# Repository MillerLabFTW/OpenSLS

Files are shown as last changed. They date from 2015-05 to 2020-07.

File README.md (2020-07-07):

# OpenSLS

#### An open-source Selective Laser Sintering platform developed at Rice University
#### Miller Lab: Physiologic Systems Engineering and Advanced Materials
#### [millerlab.rice.edu](http://millerlab.rice.edu)
&nbsp;

### Update 07/07/20
- Our latest work has been published in Nature Biomedical Engineering. Here, we adapted openSLS for laser sintering of carbohydrates, which we are using to pattern perfusable vascular networks in engineered tissues
- Learn more about this work from Rice University's [Press Release](http://news.rice.edu/2020/06/29/laser-welded-sugar-sweet-way-to-3d-print-blood-vessels-2/?fbclid=IwAR0U7sia3JYhuekfoaQjJkxIh-vBjE8x_2c2UG4KTCaLtkVJyBe03XaeHhM) or by reading [the article](https://rdcu.be/b5tHy).
- The R4 hardware designs are the final versions developed in this work

### Update 03/23/20
- We are adding a new batch of design files for openSLS -- more details to come
- Please note that the newly added R4 design is *NOT* simply an upgrade of our earlier R3 hardware. Rather, it is a version for SLS using specialty powders for biomaterials research, and uses a different mechanism for powder handling. We will add more details about this (hopefully soon!). For conventional nylon or wax SLS, R3 remains the most recent design. 

### Update 02/10/16
- We are excited to annouce that OpenSLS has been published! You can find our paper at [PLOS ONE's website](http://journals.plos.org/plosone/article?id=10.1371/journal.pone.0147399).
Many of the hardware-related details (wiring diagrams, G-code editing, Bill of Materials) are in the supporting information, which we have uploaded here.  
- We are releasing our R3 hardware update and the corresponding firmware. What's new? See below.
- A Python version of our G-code munging utility is now available, which may be more convenient than our earlier PHP implementation

### Build Documentation
This git repository includes:
- Designs for lasercut and 3D printed parts for our first (R1), second (R2), and third (R3) generations of powder handing modules
- Current firmware (with thanks to Tim Schmidt!)
- Slic3r configuration and G-code munging script for G-code creation and processing
- Wiring diagram for electronics configuration (based on RAMBo electronics)
- Model geometries we showcased in our PLOS ONE paper
- Bill of Materials

### Hardware Versions
Basic summary of our hardware verions to date:

1. R1, designed by Andreas Bastian: Proof-of-concept build for OpenSLS. Buld is almost entirely acrylic + 3D printed parts. Powder distributor is a metal rod which counter-rotates, driven by belt motion. This build has everything you need to do SLS, but it lacks a simple powder collection system.
2. R2, designed by Andreas Bastian: This was the hardware used for the entirety of our PLOS ONE paper. It is mostly made from acrylic, but has an aluminum build piston and platform amenable to heating. Distributor is a static plow (a lab spatula). Powder is collected into a hopper through ducts built into the acrylic design.
You can read more about the design upgrades Andreas made from R1 hardware to R2 hardware on the [RepRap wiki page](http://reprap.org/wiki/OpenSLS#R1_Hardware). 
3. R3, designed by Ian Kinstlinger, Anderson Ta, and David Yalacki: This is an all-acrylic build designed for low cost and simplicity. Larger powder ducts facilitate powder collection and the overall form factor is a bit smaller. Note that this build will not be compatible with any powder pre-heating, but it's been working great for our purposes. Distributor is a steel 8mm rod mounted on a pair of 608 bearings. A [DC Motor](http://www.amazon.com/Science-Wiz-Motors-Working-Voltage/dp/B000BRUHW8/ref=sr_1_2?ie=UTF8&qid=1455162773&sr=8-2&keywords=dc+motor) spins the rod to give you a rotating distributor and the whole thing is mounted on springs to adjust height.
4. R4, designed by Ian Kinstlinger and David Yalacki: This is our modified build for carbohydrate sintering. We replace the conventional two-piston design (powder reservoir and build volume) with a single piston build volume and a powder reservoir which is suspended from the 2-axis gantry which moves the laser head around. Powder is dispensed by shaking it loose from the reservoir onto the build area. 
This design helps to mitigate the relatively poor powder flowability of carbohydrates compared to standard SLS materials like nylon. More information can be found in our Nature BME publication. 

### Links
- [Nature BME carbohydrate SLS paper](https://rdcu.be/b5tHy), [supplementary information](https://static-content.springer.com/esm/art%3A10.1038%2Fs41551-020-0566-1/MediaObjects/41551_2020_566_MOESM1_ESM.pdf), and [extended datasets](https://zenodo.org/record/3723373#.XwTOOihKiUk)
- [PLOS ONE OpenSLS paper](http://journals.plos.org/plosone/article?id=10.1371/journal.pone.0147399)
- [RepRap OpenSLS wiki page](http://reprap.org/wiki/OpenSLS): Documentation of early OpenSLS builds including video

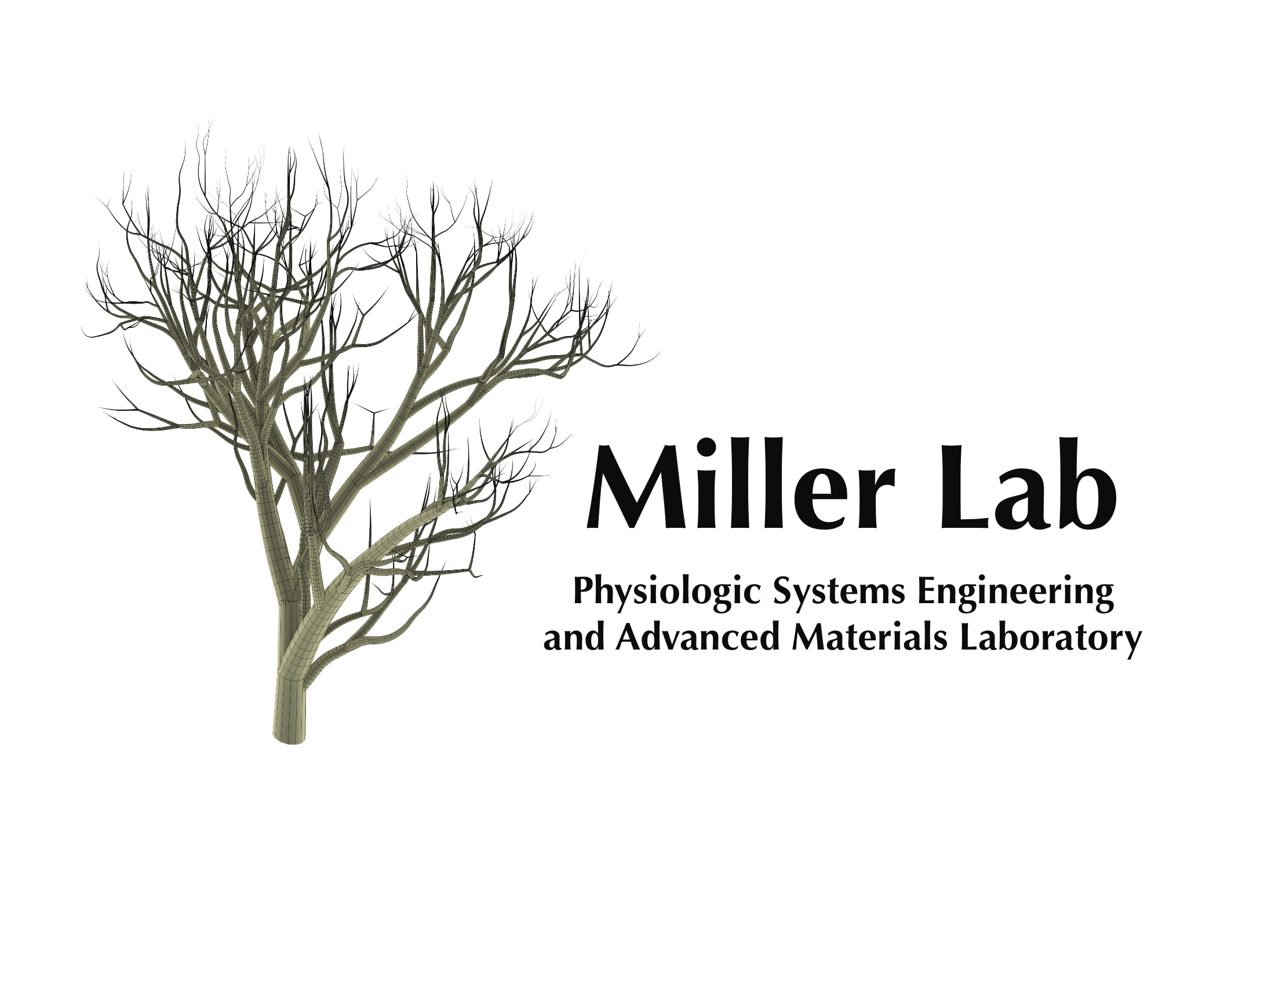
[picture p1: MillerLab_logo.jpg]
MillerLab logo


### Acknowledgements
- Thanks to [SeeMeCNC](http://www.seemecnc.com/) for helping us install and configure our laser cutter
- Thanks to Ultimachine for RAMBo support
- Thanks to the Marlin dev team and to Tim Schmidt for specially modified laser firing firmware
- Thanks to all the open-source 3D printing software that has helped us build and operate OpenSLS: Arduino, RepRap, Python, Slic3r, Netfabb, Pronterface, OpenSCAD, and more!

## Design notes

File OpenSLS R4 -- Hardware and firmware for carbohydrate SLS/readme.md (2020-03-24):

## Note

This is a complex hardware project which likely will need some adaptation for other implementations. We provide all the design files, hardware, and firmware here, and we encourage anyone interested in the project to read more details in our [PLOS One Paper](https://journals.plos.org/plosone/article?id=10.1371/journal.pone.0147399) and the associated supplementary material. If you have questions about the project or the hardware, please get in touch. Jordan Miller (jmil [at] rice [dot] edu) directs our lab group at Rice which developed this project, and Ian Kinstlinger (iankinstlinger [at] gmail [dot] com) designed most of the hardware.

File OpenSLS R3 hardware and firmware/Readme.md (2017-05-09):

Laser Cutting 
-Laser cut in 5.6mm acrylic
-These parts required ~3 sheets (18x24) for us

Marlin FW
- This version of Marlin is almost identical to our R1/R2 version. The only update is defining a MOSFET for controlling the DC motor which rotates the distributor. The DC motor is controlled by the HEAT0 pin on the RAMBo (see wiring diagram and [RAMBo wiki] (http://reprap.org/wiki/Rambo_development))
G-code for spinning the motor is M106 S### to turn on, M107 to turn off. S### is an integer 0-255 which controls speed via PWM. 

We do not have an assembly guide for this powder module at this time. But, if you are interested in building it we will be happy to help where we can.

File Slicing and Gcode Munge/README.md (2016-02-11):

The settings used for laser sintering with OpenSLS differ considerably from the typical defaults used for melt extrusion printing. 
A configuration file for Slic3r is included here.  

An important adjustment necessary in preparing geometries for OpenSLS involves scaling the model in z. 
Slic3r settings do not allow a layer height taller than the nozzle diameter, so we treat the layer height as 0.05mm in Slic3r. 
In actuality, the layer height is 0.15 (nylon) or 0.30mm (PCL). 
To compensate, the geometry needs to be scaled down in z by the scaling factor between Slic3r layer height and actual layer height. 
(For a geometry being sliced with layer height 0.05mm and sintered with layer height 0.15, 
the geometry should be shrunk by a factor of 3 in the z-axis (Netfabb Basic))

Summary of configuration:

Parameter	Value		Parameter	Value
Layer height	0.05mm		   		Infill density	Variable – we often used 20%
First layer height	0.05mm			Fill pattern	Concentric
Perimeters (min)	0		I	Infill every 1 layers
Horizontal Shells	0 (Top & Bottom)	Solid infill every 0 layers
Extra perimeters if needed	No		Support material	Disable
Detect thin walls	Yes			Skirt	0 loops
Detect bridging perimeters	Yes		Brim width	0mm
Speed: perimeters	30mm/s			Bed Size	X: 70 Y: 70 mm
Speed: infill	60mm/s				Bed Center 	X: 35 Y: 35 mm
Speed: travel	130mm/s				Nozzle Diameter	0.075mm (laser spot size)
First layer speed	50%			

G-code Munging
The G-code output from slicing an STL model is meant to be interpreted by a melt extrusion printer, not SLS. 
Thus, the G-code must be modified so that Z changes invoke the addition of a new powder layer and XY motion is 
assigned the appropriate laser firing behavior. 

##New Python munging script

We wrote a simple Python script to perform the necessary G-code edits. It is described in detail in our Supporting Information file for our PLOS ONE paper and posted here.
Simply run the Python script and you will be prompted to choose a file to munge.

A neat function of the new munge script is the ability to slice laser power settings into the geometry. This is done by associating extruders in Slic3r with power settings in the munge script. 

## Old PHP script

We performed munging (data editing) of the G-code with a custom 
PHP script that is available on the OpenSLS Github repository. The PHP script is run from the command line as 
follows (example in Windows operating system):

> cd C:\TargetDirectory
> “C:\...\PHP\php.exe” “C:\...\Munge\munge.php” –i “C:\...\file.gcode”

This results in the creation of the modified G-code file in TargetDirectory with the name output.gcode.

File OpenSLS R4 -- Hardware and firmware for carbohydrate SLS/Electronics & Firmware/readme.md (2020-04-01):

Note about the wiring diagram and firmware:

There are two electronics boards and two firmware files because we set up the hardware to use a main controller board (RAMBo) with a secondary (slave) Arduino board (Mega in our setup, but an Uno or even a nano would work). The sole purpose of the slave Arduino is to drive the servo motor which raises and lowers the powder spreader. In theory there is no reason that this servo can't run off another MOSFET on the RAMBo, but we were getting very noisy signal which caused the spreader to vibrate excessively. Running a second board provides enough isolation, and the slave Arduino just gets PWM signals from the primary RAMBo that indicate when to move the servo. Custom GCODE M166 was added to drive the servo based on a PWM value (e.g. use M166 S##).

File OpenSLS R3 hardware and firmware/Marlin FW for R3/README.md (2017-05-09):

Fork of Jordan Miller's fork of Erik Zalm's Marlin here modified to control a laser 
cutter's gantry and laser.

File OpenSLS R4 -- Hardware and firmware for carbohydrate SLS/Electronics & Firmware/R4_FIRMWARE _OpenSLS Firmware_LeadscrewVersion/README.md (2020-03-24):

==========================
Marlin 3D Printer Firmware
==========================
Marlin has a GPL license because I believe in open development.
Please do not use this code in products (3D printers, CNC etc) that are closed source or are crippled by a patent.



Quick Information
===================
This RepRap firmware is a mashup between <a href="https://github.com/kliment/Sprinter">Sprinter</a>, <a href="https://github.com/simen/grbl/tree">grbl</a> and many original parts.

Derived from Sprinter and Grbl by Erik van der Zalm.
Sprinters lead developers are Kliment and caru.
Grbls lead developer is Simen Svale Skogsrud. Sonney Jeon (Chamnit) improved some parts of grbl
A fork by bkubicek for the Ultimaker was merged, and further development was aided by him.
Some features have been added by:
Lampmaker, Bradley Feldman, and others...

Features:

*   Interrupt based movement with real linear acceleration
*   High steprate
*   Look ahead (Keep the speed high when possible. High cornering speed)
*   Interrupt based temperature protection
*   preliminary support for Matthew Roberts advance algorithm
    For more info see: http://reprap.org/pipermail/reprap-dev/2011-May/003323.html
*   Full endstop support
*   SD Card support
*   SD Card folders (works in pronterface)
*   SD Card autostart support
*   LCD support (ideally 20x4)
*   LCD menu system for autonomous SD card printing, controlled by an click-encoder.
*   EEPROM storage of e.g. max-velocity, max-acceleration, and similar variables
*   many small but handy things originating from bkubicek's fork.
*   Arc support
*   Temperature oversampling
*   Dynamic Temperature setpointing aka "AutoTemp"
*   Support for QTMarlin, a very beta GUI for PID-tuning and velocity-acceleration testing. https://github.com/bkubicek/QTMarlin
*   Endstop trigger reporting to the host software.
*   Updated sdcardlib
*   Heater power reporting. Useful for PID monitoring.
*   PID tuning
*   CoreXY kinematics (www.corexy.com/theory.html)
*   Delta kinematics
*   Dual X-carriage support for multiple extruder systems
*   Configurable serial port to support connection of wireless adaptors.
*   Automatic operation of extruder/cold-end cooling fans based on nozzle temperature
*   RC Servo Support, specify angle or duration for continuous rotation servos.

The default baudrate is 250000. This baudrate has less jitter and hence errors than the usual 115200 baud, but is less supported by drivers and host-environments.

Differences and additions to the already good Sprinter firmware:
================================================================

*Look-ahead:*

Marlin has look-ahead. While sprinter has to break and re-accelerate at each corner,
lookahead will only decelerate and accelerate to a velocity,
so that the change in vectorial velocity magnitude is less than the xy_jerk_velocity.
This is only possible, if some future moves are already processed, hence the name.
It leads to less over-deposition at corners, especially at flat angles.

*Arc support:*

Slic3r can find curves that, although broken into segments, were ment to describe an arc.
Marlin is able to print those arcs. The advantage is the firmware can choose the resolution,
and can perform the arc with nearly constant velocity, resulting in a nice finish.
Also, less serial communication is needed.

*Temperature Oversampling:*

To reduce noise and make the PID-differential term more useful, 16 ADC conversion results are averaged.

*AutoTemp:*

If your gcode contains a wide spread of extruder velocities, or you realtime change the building speed, the temperature should be changed accordingly.
Usually, higher speed requires higher temperature.
This can now be performed by the AutoTemp function
By calling M109 S<mintemp> T<maxtemp> F<factor> you enter the autotemp mode.

You can leave it by calling M109 without any F.
If active, the maximal extruder stepper rate of all buffered moves will be calculated, and named "maxerate" [steps/sec].
The wanted temperature then will be set to t=tempmin+factor*maxerate, while being limited between tempmin and tempmax.
If the target temperature is set manually or by gcode to a value less then tempmin, it will be kept without change.
Ideally, your gcode can be completely free of temperature controls, apart from a M109 S T F in the start.gcode, and a M109 S0 in the end.gcode.

*EEPROM:*

If you know your PID values, the acceleration and max-velocities of your unique machine, you can set them, and finally store them in the EEPROM.
After each reboot, it will magically load them from EEPROM, independent what your Configuration.h says.

*LCD Menu:*

If your hardware supports it, you can build yourself a LCD-CardReader+Click+encoder combination. It will enable you to realtime tune temperatures,
accelerations, velocities, flow rates, select and print files from the SD card, preheat, disable the steppers, and do other fancy stuff.
One working hardware is documented here: http://www.thingiverse.com/thing:12663
Also, with just a 20x4 or 16x2 display, useful data is shown.

*SD card folders:*

If you have an SD card reader attached to your controller, also folders work now. Listing the files in pronterface will show "/path/subpath/file.g".
You can write to file in a subfolder by specifying a similar text using small letters in the path.
Also, backup copies of various operating systems are hidden, as well as files not ending with ".g".

*SD card folders:*

If you place a file auto[0-9].g into the root of the sd card, it will be automatically executed if you boot the printer. The same file will be executed by selecting "Autostart" from the menu.
First *0 will be performed, than *1 and so on. That way, you can heat up or even print automatically without user interaction.

*Endstop trigger reporting:*

If an endstop is hit while moving towards the endstop, the location at which the firmware thinks that the endstop was triggered is outputed on the serial port.
This is useful, because the user gets a warning message.
However, also tools like QTMarlin can use this for finding acceptable combinations of velocity+acceleration.

*Coding paradigm:*

Not relevant from a user side, but Marlin was split into thematic junks, and has tried to partially enforced private variables.
This is intended to make it clearer, what interacts which what, and leads to a higher level of modularization.
We think that this is a useful prestep for porting this firmware to e.g. an ARM platform in the future.
A lot of RAM (with enabled LCD ~2200 bytes) was saved by storing char []="some message" in Program memory.
In the serial communication, a #define based level of abstraction was enforced, so that it is clear that
some transfer is information (usually beginning with "echo:"), an error "error:", or just normal protocol,
necessary for backwards compatibility.

*Interrupt based temperature measurements:*

An interrupt is used to manage ADC conversions, and enforce checking for critical temperatures.
This leads to less blocking in the heater management routine.

Implemented G Codes:
====================

*  G0  -> G1
*  G1  - Coordinated Movement X Y Z E
*  G2  - CW ARC
*  G3  - CCW ARC
*  G4  - Dwell S<seconds> or P<milliseconds>
*  G10 - retract filament according to settings of M207
*  G11 - retract recover filament according to settings of M208
*  G28 - Home all Axis
*  G90 - Use Absolute Coordinates
*  G91 - Use Relative Coordinates
*  G92 - Set current position to cordinates given

M Codes
*  M0   - Unconditional stop - Wait for user to press a button on the LCD (Only if ULTRA_LCD is enabled)
*  M1   - Same as M0
*  M17  - Enable/Power all stepper motors
*  M18  - Disable all stepper motors; same as M84
*  M20  - List SD card
*  M21  - Init SD card
*  M22  - Release SD card
*  M23  - Select SD file (M23 filename.g)
*  M24  - Start/resume SD print
*  M25  - Pause SD print
*  M26  - Set SD position in bytes (M26 S12345)
*  M27  - Report SD print status
*  M28  - Start SD write (M28 filename.g)
*  M29  - Stop SD write
*  M30  - Delete file from SD (M30 filename.g)
*  M31  - Output time since last M109 or SD card start to serial
*  M32  - Select file and start SD print (Can be used when printing from SD card)
*  M42  - Change pin status via gcode Use M42 Px Sy to set pin x to value y, when omitting Px the onboard led will be used.
*  M80  - Turn on Power Supply
*  M81  - Turn off Power Supply
*  M82  - Set E codes absolute (default)
*  M83  - Set E codes relative while in Absolute Coordinates (G90) mode
*  M84  - Disable steppers until next move, or use S<seconds> to specify an inactivity timeout, after which the steppers will be disabled.  S0 to disable the timeout.
*  M85  - Set inactivity shutdown timer with parameter S<seconds>. To disable set zero (default)
*  M92  - Set axis_steps_per_unit - same syntax as G92
*  M104 - Set extruder target temp
*  M105 - Read current temp
*  M106 - Fan on
*  M107 - Fan off
*  M109 - Sxxx Wait for extruder current temp to reach target temp. Waits only when heating
*         Rxxx Wait for extruder current temp to reach target temp. Waits when heating and cooling
*  M114 - Output current position to serial port
*  M115 - Capabilities string
*  M117 - display message
*  M119 - Output Endstop status to serial port
*  M126 - Solenoid Air Valve Open (BariCUDA support by jmil)
*  M127 - Solenoid Air Valve Closed (BariCUDA vent to atmospheric pressure by jmil)
*  M128 - EtoP Open (BariCUDA EtoP = electricity to air pressure transducer by jmil)
*  M129 - EtoP Closed (BariCUDA EtoP = electricity to air pressure transducer by jmil)
*  M140 - Set bed target temp
*  M190 - Sxxx Wait for bed current temp to reach target temp. Waits only when heating
*         Rxxx Wait for bed current temp to reach target temp. Waits when heating and cooling
*  M200 - Set filament diameter
*  M201 - Set max acceleration in units/s^2 for print moves (M201 X1000 Y1000)
*  M202 - Set max acceleration in units/s^2 for travel moves (M202 X1000 Y1000) Unused in Marlin!!
*  M203 - Set maximum feedrate that your machine can sustain (M203 X200 Y200 Z300 E10000) in mm/sec
*  M204 - Set default acceleration: S normal moves T filament only moves (M204 S3000 T7000) im mm/sec^2  also sets minimum segment time in ms (B20000) to prevent buffer underruns and M20 minimum feedrate
*  M205 -  advanced settings:  minimum travel speed S=while printing T=travel only,  B=minimum segment time X= maximum xy jerk, Z=maximum Z jerk, E=maximum E jerk
*  M206 - set additional homeing offset
*  M207 - set retract length S[positive mm] F[feedrate mm/sec] Z[additional zlift/hop]
*  M208 - set recover=unretract length S[positive mm surplus to the M207 S*] F[feedrate mm/sec]
*  M209 - S<1=true/0=false> enable automatic retract detect if the slicer did not support G10/11: every normal extrude-only move will be classified as retract depending on the direction.
*  M218 - set hotend offset (in mm): T<extruder_number> X<offset_on_X> Y<offset_on_Y>
*  M220 S<factor in percent>- set speed factor override percentage
*  M221 S<factor in percent>- set extrude factor override percentage
*  M240 - Trigger a camera to take a photograph
*  M280 - Position an RC Servo P<index> S<angle/microseconds>, ommit S to report back current angle
*  M300 - Play beepsound S<frequency Hz> P<duration ms>
*  M301 - Set PID parameters P I and D
*  M302 - Allow cold extrudes
*  M303 - PID relay autotune S<temperature> sets the target temperature. (default target temperature = 150C)
*  M304 - Set bed PID parameters P I and D
*  M400 - Finish all moves
*  M500 - stores paramters in EEPROM
*  M501 - reads parameters from EEPROM (if you need reset them after you changed them temporarily).
*  M502 - reverts to the default "factory settings".  You still need to store them in EEPROM afterwards if you want to.
*  M503 - print the current settings (from memory not from eeprom)
*  M540 - Use S[0|1] to enable or disable the stop SD card print on endstop hit (requires ABORT_ON_ENDSTOP_HIT_FEATURE_ENABLED)
*  M600 - Pause for filament change X[pos] Y[pos] Z[relative lift] E[initial retract] L[later retract distance for removal]
*  M907 - Set digital trimpot motor current using axis codes.
*  M908 - Control digital trimpot directly.
*  M350 - Set microstepping mode.
*  M351 - Toggle MS1 MS2 pins directly.
*  M928 - Start SD logging (M928 filename.g) - ended by M29
*  M999 - Restart after being stopped by error

Configuring and compilation:
============================

Install the arduino software IDE/toolset v23 (Some configurations also work with 1.x.x)
   http://www.arduino.cc/en/Main/Software

For gen6/gen7 and sanguinololu the Sanguino directory in the Marlin dir needs to be copied to the arduino environment.
  copy ArduinoAddons\Arduino_x.x.x\sanguino <arduino home>\hardware\Sanguino

Copy the Marlin firmware
   https://github.com/ErikZalm/Marlin/tree/Marlin_v1
   (Use the download button)

Start the arduino IDE.
Select Tools -> Board -> Arduino Mega 2560    or your microcontroller
Select the correct serial port in Tools ->Serial Port
Open Marlin.pde

Click the Verify/Compile button

Click the Upload button
If all goes well the firmware is uploading

That's ok.  Enjoy Silky Smooth Printing.

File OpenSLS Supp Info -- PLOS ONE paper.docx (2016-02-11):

Supporting Information for

Open-source Selective Laser Sintering (OpenSLS) of Nylon and Biocompatible Polycaprolactone

Ian S. Kinstlinger*, Andreas Bastian*, Samantha J. Paulsen, Daniel H. Hwang,

Anderson Ta, David R. Yalacki, Tim Schmidt, and Jordan S. Miller

Department of Bioengineering, Rice University, Houston, Texas, USA

Materials and Configuration of OpenSLS

Bill of Materials

The bill of materials for OpenSLS is provided (S1 Bill of Materials), and can also be found on the OpenSLS github repository (https://github.com/MillerLabFTW/OpenSLS). Future updates to the design files or firmware for OpenSLS will be made available through this repository. The exact dimensions of components may depend on the laser cutter that is used. For example, the dimensions for the laser-cut powder module might require adjustment.

Wiring

Caution: extreme care should be taken when modifying the wiring of the laser and its power supply. Laser power supplies operate with voltages on the order of tens of kilovolts and may hold charge for some time after being powered down.

Figure A shows the wiring diagram used for OpenSLS. The motors illustrated to the left of the RAMBo board are the NEMA17 motors that are part of the powder handing module, while the motor drivers shown to the right drive the native stepper motors inside the laser cutter. Matching the ground planes for the laser power supply, stepper drivers, and RAMBo board is critical.

Firmware

OpenSLS uses a customized version of the widely used open-source Marlin for Arduino, available through the github repository. We have configured the firmware to disable features irrelevant to OpenSLS (e.g. temperature control, endstop detection, servo support). We added functionalities corresponding to features of SLS, and extended the firmware's G-code machine language to accommodate the new functions (Table A).

Initially, laser firing and extinguishing were implemented in Marlin (Marlin_main.cpp), in the G-code processing routine. Laser firing and extinguishing were functional, but their timing relative to other machine operations wasn't satisfactory. Laser intensity control was moved to a 16 bit timer, chosen automatically based on the setting of LASER_INTENSITY_PIN in pins.h. Laser firing and extinguishing execution were moved to the stepper driver interrupt handler, where G-codes are ultimately evaluated, requiring the addition of laser-specific parameters to the firmware's command buffer. A counter tracking laser firing time was added and is stored in the microcontroller's EEPROM to maintain persistence across power cycles. An L axis was added to Marlin’s base 5-axis configuration (X, Y, Z, E0 and E1 axes) to facilitate calculation of laser pulses per millimeter. A runtime-configurable laser debugging mode with verbose serial output was added. Laser-related menu items were added for the “LCD Smart Controller” and “Full Graphic LCD Smart Controller”. Lastly, laser firing, extinguishing, and maintanance functions were consolidated in laser.h and laser.cpp

The implementation permits laser operation in three distinct firing modes:

1) Continuous mode: the laser is turned on and remains on at the selected intensity until it receives a G-code instructing it to turn off. Continuous mode firing has been used for all OpenSLS firing commands at this time.
2) Pulsed mode: the laser fires punctuated bursts at intervals matching P: PULSES_PER_MM, each lasting for L: DURATION (in μs). The values of P and L are specified within the laser firing G-code (see Table A) so that the timing and duration of the laser pulses can be easily added to the firmware's command buffer with the laser firing command. This allows us the laser to be fired and extinguished from the inner loop of the stepper driver interrupt handler, enabling microstep-accurate positioning and accurate timing of laser pulses.
3) Raster mode: a special variation of pulsed mode which accepts an intensity value for each pulse in a variable-length horizontal line of evenly spaced pulses, with configurable pulse offsets in X and Y axes, arbitrary line-advance, and selectable left or right rastering. Like pulsed mode, timing is performed in the stepper driver interrupt handler, and the information necessary for many pulses is contained in a single command, allowing for very precise high-speed control. A possible future development within this mode is support for rastering along an arbitrary line in 3D space.

We also implemented several new compile-time configuration options in the firmware:

LASER_CONTROL: When set to 1, the LASER_FIRE pin supplies a PWM signal at frequency specified by LASER_PWM in Configuration.h. The duty cycle of the wave is adjusted to control intensity, logic level LOW is set when off. This configuration works well for controlling common laser diodes. When set to 2, the LASER_FIRE pin supplies a logic level signal HIGH for fire, LOW for extinguish. The LASER_INTENSITY pin supplies a PWM signal at frequency specified by LASER_PWM in Configuration.h, and duty cycle of the wave is adjusted to control intensity.

LASER_FIRE_G1: G0 moves the laser to a specified set of coordinates without firing, a G1 command moves the laser to the specified coordinates while firing.

LASER_FIRE_SPINDLE: M3 turns the laser on in place, without requiring it to move. M5 turns the laser off in place.

LASER_FIRE_E: Any movement in the E axis (which represents the extruder when controlling a 3D printer) fires the laser. In this way, the laser can make use of unmodified G-code generated for 3D printers. Note: this mode is not recommended in OpenSLS because extruder axes are already controlling the power reservoir and build platform motors.

Table A shows the specific G-codes added in our firmware and their functions. An excellent resource for the standard G-code language used in this firmware to control OpenSLS can be found on the RepRap wiki (reprap.org/wiki/G-code).

G-code | Function | Notes
G1 | Move while laser firing | In unmodified Marlin, G0 and G1 refer to the same action.
G0 | Move while laser off
M3 | Laser on (fire) | A G1 command will fire the laser on its own and does not need to be preceded by an M3 command
M5 | Laser off (extinguish)
M649 | Modify laser settings | This command takes the format “M649 S# L# P# D# B#” S: Intensity of laser firing (0-100.0%) L: Duration of firing (in microseconds) P: Pulse per mm (in pulse mode) D: Diagnostic mode (0 = off; 1 = on) B: Laser firing mode (0 = continuous, 1 = pulsed, 2 = raster) This command can be used to set laser settings before starting to sinter, or to adjust settings during sintering.

Table A. G-codes unique to OpenSLS and their functions

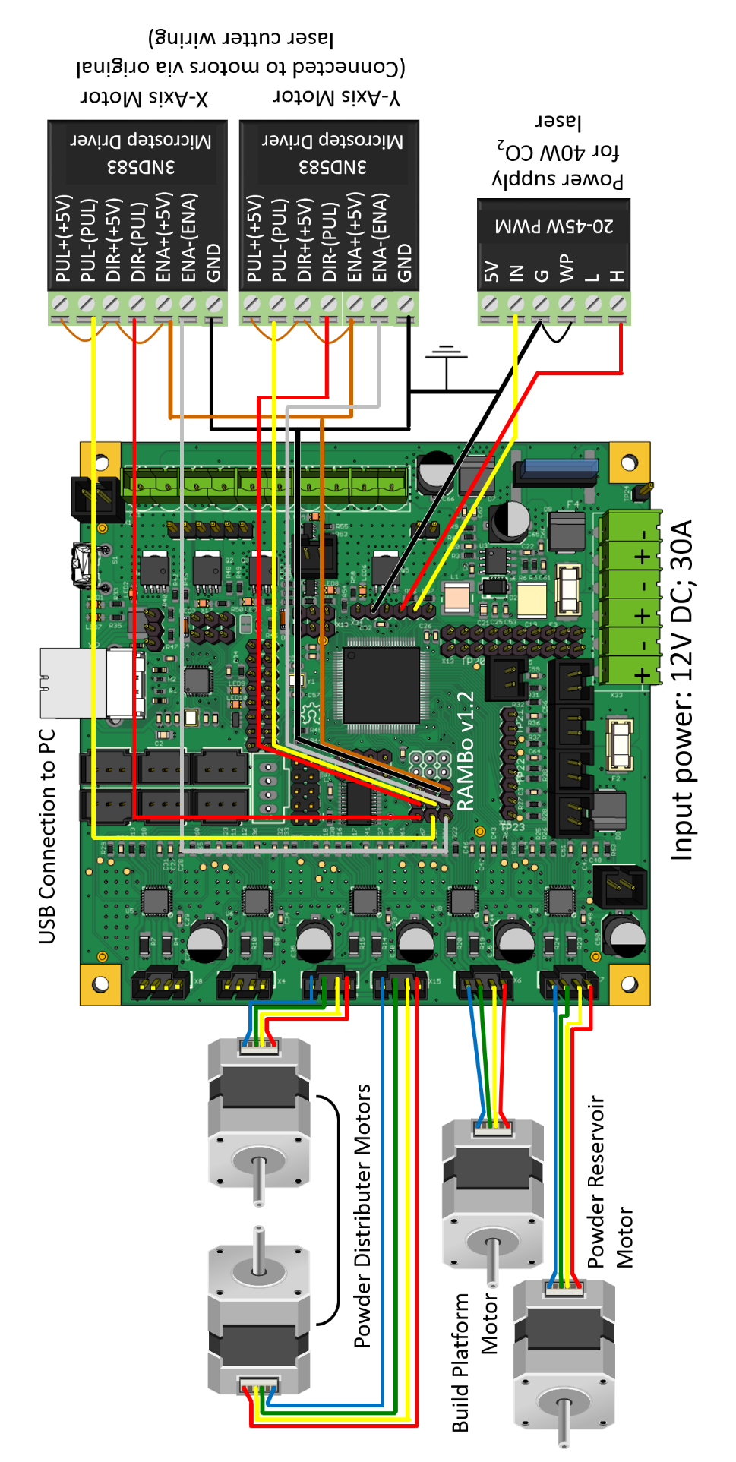
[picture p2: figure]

Figure A. Wiring diagram for OpenSLS. X and Y axis motor controls used Leadshine microstep drivers already onboard the laser cutter. The 40W laser power supply replaced the 80W supply natively integrated with the laser cutter. Plow motors (RAMBo Z-axis) and powder-handing piston motors (RAMBo E0- and E1-axes) are standard NEMA17 stepper motors. OpenSLS’s custom hardware configuration requires a modified version of typical open-source 3DP firmware which re-maps X and Y control to the motor extension pins and implements laser control via the PWM pins.

Slicing Settings in Slic3r Software

The settings used for laser sintering with OpenSLS differ considerably from the typical defaults used for melt extrusion printing. A configuration file for the open-source Slic3r software (slic3r.org) is included on the OpenSLS github repository, and the settings are indicated in Table B. An important adjustment necessary in preparing geometries for OpenSLS involves scaling the model along its z-axis. Slic3r settings do not allow a layer height taller than the nozzle diameter, so we treat the layer height as 0.05mm in Slic3r. In actuality, the layer height is 0.15 (nylon) or 0.30mm (PCL). To compensate, the geometry needs to be scaled down in z by the scaling factor between Slic3r layer height and actual layer height. For example, a model sliced with layer height 0.05mm and sintered with layer height 0.15 should be shrunk by a factor of 3 in the z-axis (Netfabb Basic, netfabb.com).

Parameter | Value | | Parameter | Value
Layer height | 0.05 mm | | Infill density | Variable – we often used 20%
First layer height | 0.05 mm | | Fill pattern | Concentric
Perimeters (min) | 0 | | Infill every 1 layers
Horizontal Shells | 0 (Top & Bottom) | | Solid infill every 0 layers
Extra perimeters if needed | No | | Support material | Disable
Detect thin walls | Yes | | Skirt | 0 loops
Detect bridging perimeters | Yes | | Brim width | 0 mm
Speed: perimeters | 30 mm/s | | Bed Size | X: 70 Y: 70 mm
Speed: infill | 60 mm/s | | Bed Center | X: 35 Y: 35 mm
Speed: travel | 130 mm/s | | Nozzle Diameter | 0.075 mm
First layer speed | 50%

Table B. Parameters used for slicing for nylon in Slic3r version 1.1.7. A .ini configuration file with these parameters is available on the OpenSLS github.

G-code Munging

The G-code output from slicing an STL model is meant to be interpreted by a melt extrusion printer, not SLS. Thus, the G-code must be modified so that Z changes invoke the addition of a new powder layer and XY motion is assigned the appropriate laser firing behavior. We performed munging (data editing) of the G-code with a custom PHP script that is available on the OpenSLS Github repository. The PHP script is run from the command line as follows (example in Windows operating system):

> cd C:\TargetDirectory

> “C:\...\PHP\php.exe” “C:\...\Munge\munge.php” –i “C:\...\file.gcode”

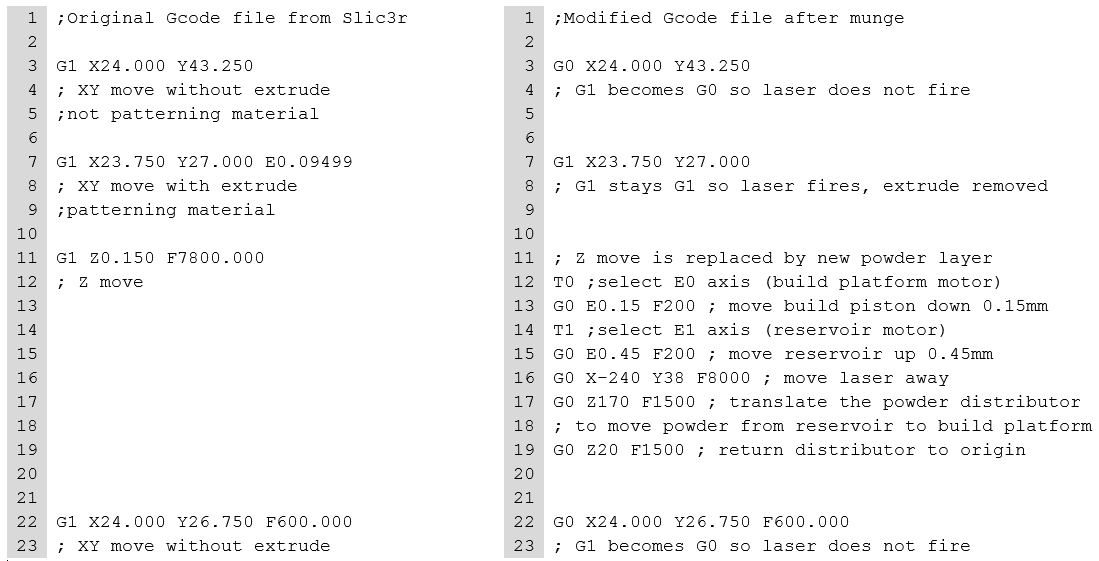
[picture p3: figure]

This results in the creation of the modified G-code in TargetDirectory with the name output.gcode. An example of G-code before and after munging is shown in Box A.

Box A. Sample G-code before and after munging for OpenSLS compatibility

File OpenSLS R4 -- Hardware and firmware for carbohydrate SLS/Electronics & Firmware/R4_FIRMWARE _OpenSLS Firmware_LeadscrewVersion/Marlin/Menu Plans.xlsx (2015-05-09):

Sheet: Menus V1
Main Screen | Prepare | Control | Card Menu | Move Axis | Temperature | Motion | Preheat PLA Settings | Preheat ABS Settings
Watch | Main | Main | Main | Prepare | Control | Control | Temperature | Temperature
Prepare | Autostart | Temperature | Refresh | X: | Nozzle | Acc: | Fan Speed | Fan Speed
Control | Disable Steppers | Motion |  | Y: | Autotemp | VXY-Jerk | Nozzle | Nozzle
Card Menu | AutoHome | Store Memory |  | Z: | Min | Vmax-X | Bed | Bed
 | Set Origin | Load Memory |  | Extrude | Max | Vmax-Y | Store Settings | Store Settings
 | Preheat PLA | Restore Failsafe |  | Extract | Fact | Vmax-Z
 | Preheat ABS |  |  |  | Bed | Vmax-E
 | Cooldown |  |  |  | Fan Speed | Vtrav-min
 | Move Axis |  |  |  | PID-P | Vmin
 |  |  |  |  | PID-I | Amax-X
 |  |  |  |  | PID_D | Amax-X
 |  |  |  |  | PID-C | Amax-X
 |  |  |  |  | Preheat PLA Settings | Amax-X
 |  |  |  |  | Preheat ABS Settings | A-retract
 |  |  |  |  |  | Xsteps/mm
 |  |  |  |  |  | Ysteps/mm
 |  |  |  |  |  | Zsteps/mm
 |  |  |  |  |  | Esteps/mm

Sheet: Menu Tree
Marlin LCD Menu Tree (V1)

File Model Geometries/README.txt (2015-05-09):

In this folder are the model geometries explored in the paper. 

1. Diagrid model (.stl file only)
Source: nervoussystem (n-e-r-v-o-u-s.com)
http://www.thingiverse.com/thing:7045

2. Diamond lattice model (.scad and .stl files)
Source: http://www.thingiverse.com/thing:13601/#files 

3. Reduced diamond lattice model (.scad and .stl files)
Source: http://www.thingiverse.com/thing:13601/#files, modified by Ian Kinstlinger

Note: we found printing the reduced diamond lattice (in polycaprolactone) easier when it was surrounded by a bounding box (prevents powder disturbance by distributor)
- See Reduced_diamond_lattice_in_box.stl

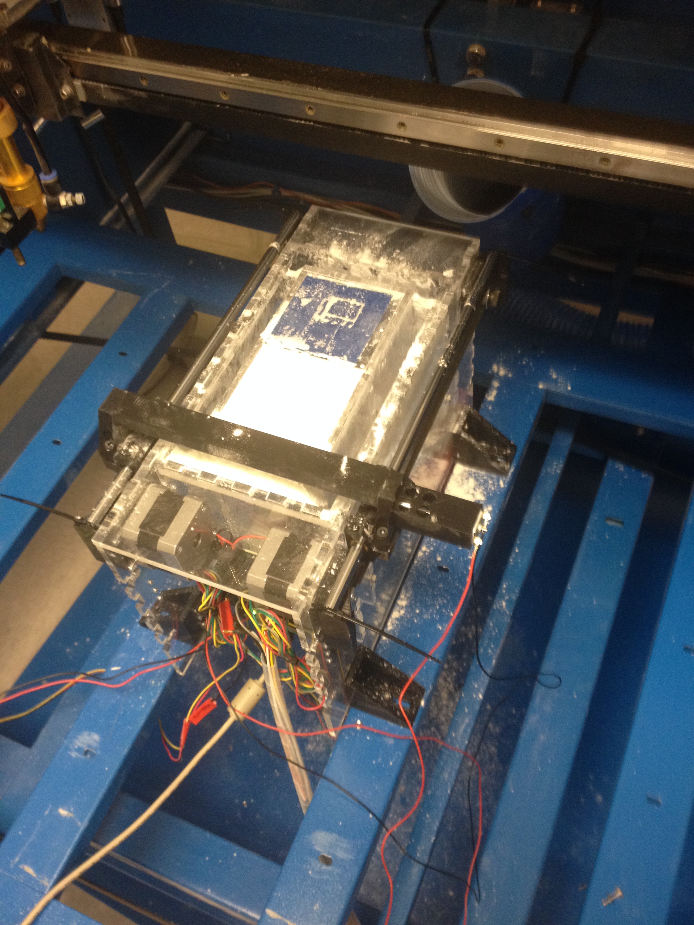
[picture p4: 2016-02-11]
OpenSLS R3 hardware and firmware/Photos/R3-1.JPG

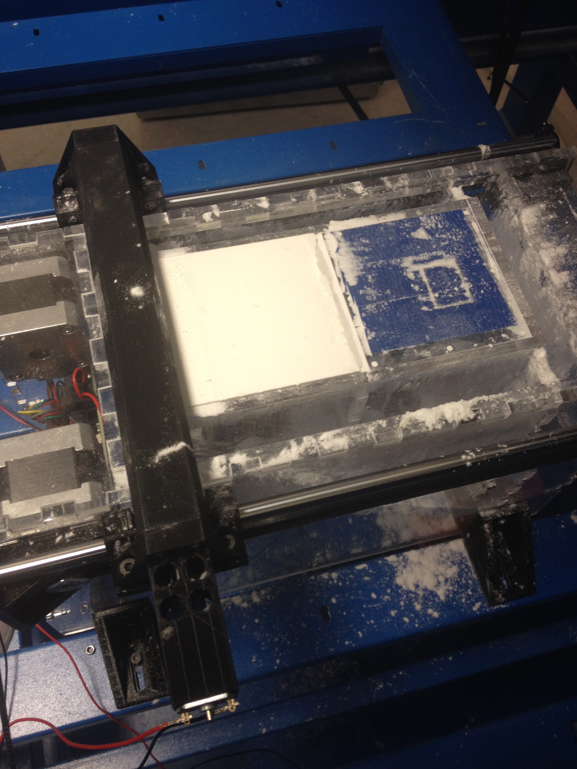
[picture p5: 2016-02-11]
OpenSLS R3 hardware and firmware/Photos/R3-6.JPG

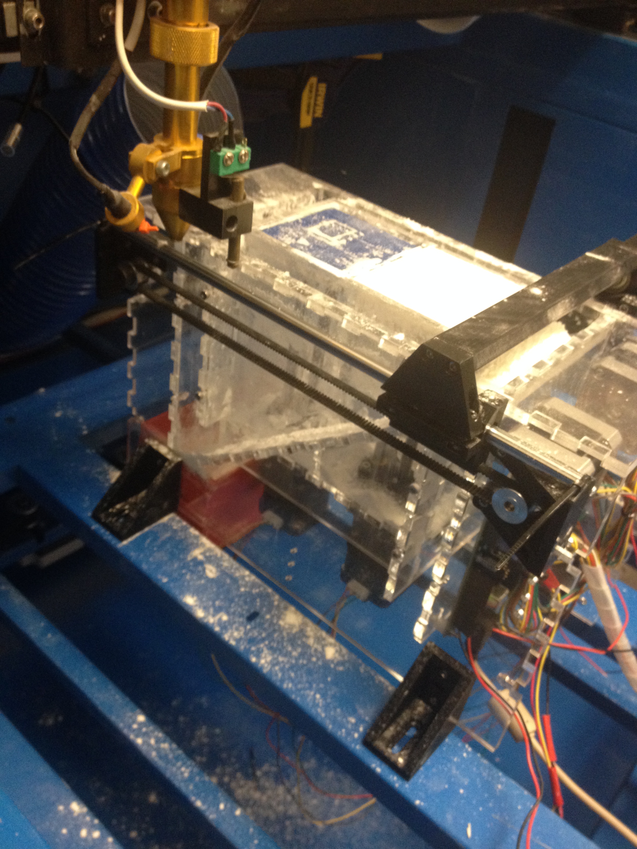
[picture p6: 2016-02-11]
OpenSLS R3 hardware and firmware/Photos/R3-3.JPG

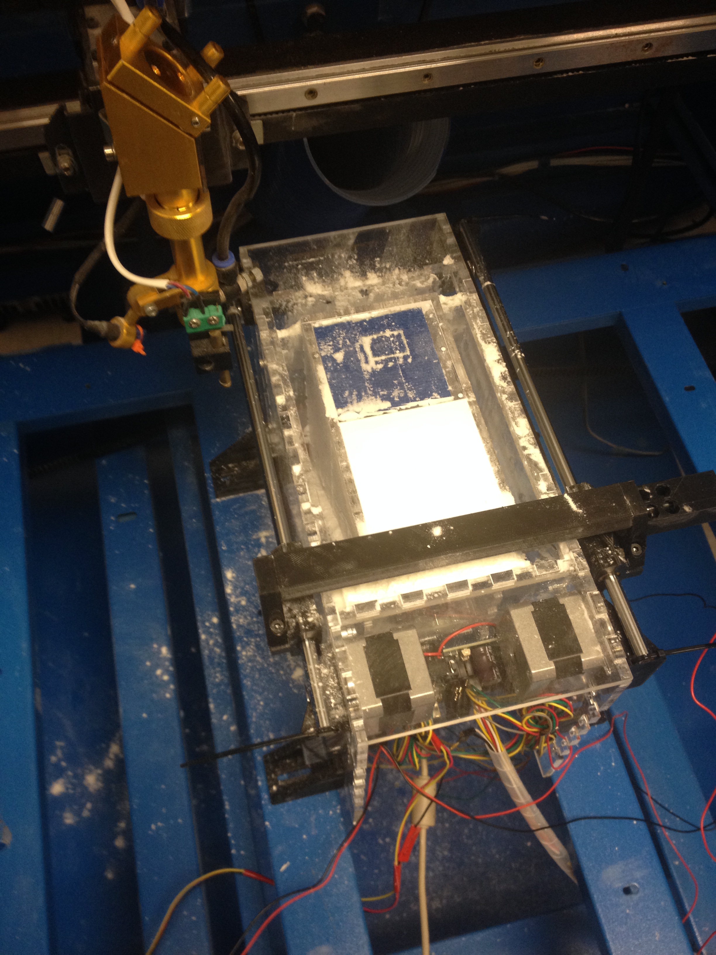
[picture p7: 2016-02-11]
OpenSLS R3 hardware and firmware/Photos/R3-2.JPG

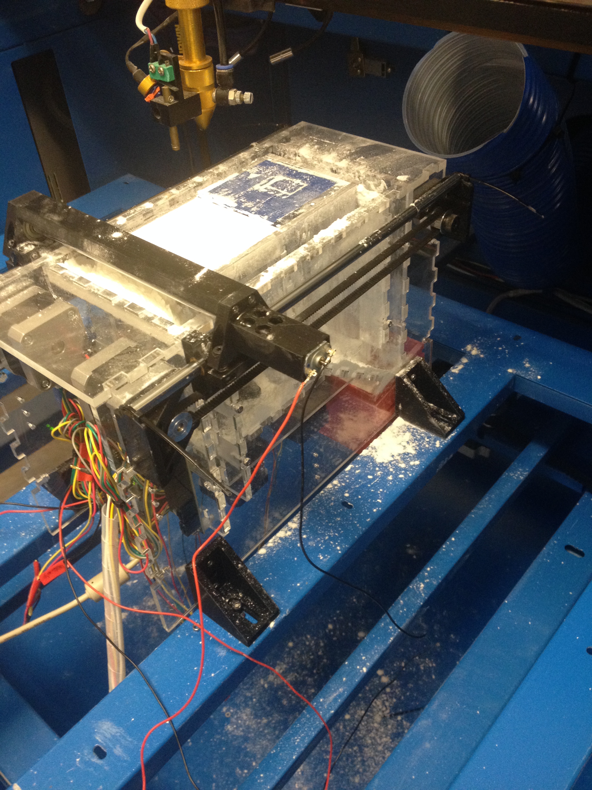
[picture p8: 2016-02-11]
OpenSLS R3 hardware and firmware/Photos/R3-4.JPG

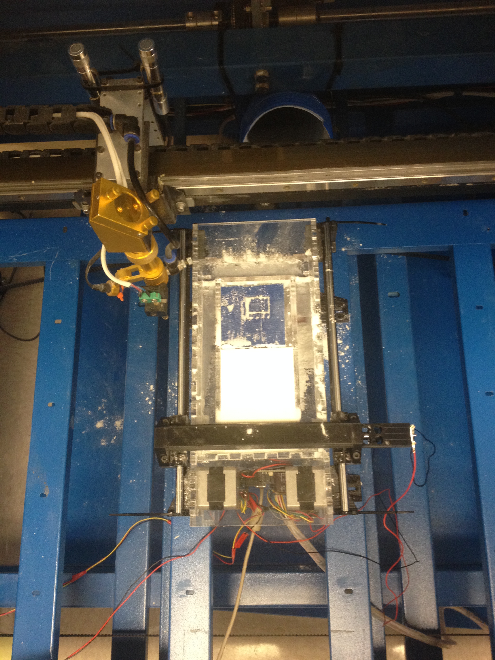
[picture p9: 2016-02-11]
OpenSLS R3 hardware and firmware/Photos/R3-5.JPG

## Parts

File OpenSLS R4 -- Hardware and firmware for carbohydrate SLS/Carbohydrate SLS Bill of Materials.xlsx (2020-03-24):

 | OpenSLS Bill of Materials (Carbohydrate SLS hardware)
Quantity | Item | Vendor | Part No | Cost Per Item ($) | Total Cost ($) | Notes
1 | 80 Watt CO2 Laser Cutter 600x900mm | SeeMeCNC.com |  | 7499.00 | 7499.00 | Any stepper motor-driver laser cutter should be suitable. We purchased an 80W laser cutter but swapped the 80W tube/power supply for a 40W.
1 | 20W PWM CO2 Laser Power Supply | LightObject.com | LSR-JN40W-1V | 205.00 | 205.00 | To replace the original 80W laser tube. No specific laser tube is required for OpenSLS. Use extreme caution if replacing a laser tube and read up on safety beforehand (http://www.repairfaq.org/sam/lasersaf.htm)
1 | 20W CO2 Sealed Laser Tube | LightObject.com | LSR-JLD20WCO2 | 220.00 | 220.00
1 | RAMBo | Ultimachine | UMRAMBOPAC13 | 170.00 | 170.00
1 | Arduino board (e.g. Arduino Uno or Arduino Mega) | Adafruit.com | 50 | 24.95 | 24.95 | Any Arduino board will suffice
1 | 12V laptop power supply | http://www.amazon.com/900A-900HA-900HD-900SD-904HA/dp/B0079G7F4M |  | 2.39 | 2.39 | Or get a block 12V/30A power supply (http://www.amazon.com/360w-Regulated-Switching-Power-Supply/dp/B0089VIBL2)
1 | DC Female Power Plug to 2 Pin Terminal (Screw Down) Adapter | Cable Wholesale | 30W1-00210 | 0.75 | 0.75
50 | 18 AWG Power Wire (by the foot) | http://www.superbrightleds.com/moreinfo/led-vehicle-replacement-bulbs/18-awg-two-conductor-power-wire/535/ | WP18-2 | 0.19 | 9.50
50 | 14 AWG Power Wire (by the foot) | http://www.superbrightleds.com/moreinfo/led-vehicle-replacement-bulbs/14-awg-two-conductor-power-wire/775/ | WDRB14-2 | 0.49 | 24.50
2 | 2.54mm 1x4 Connector & Housing Kit - 5 pack | Ultimachine | UM1X4CBCN | 3.00 | 6.00
1 | Pluggable Terminal Block, 4 contacts | Ultimachine | UMTBLK4PLUG | 3.30 | 3.30
1 | Smart LCD Controller XXL | Reprapdiscount.com |  | 69.00 | 69.00 | To run g-code files from an SD card
1 | 5V 2A Switching Power Supply w/ USB-A Connector | Adafruit.com | 1994 | 6.95 | 6.95 | Power supply for servo motor
1 | Micro Step Motor Nema 8 Bipolar Stepper Motor 0.6A 5.7oz.in/4Ncm DIY Robot | Amazon | https://www.amazon.com/Micro-Motor-Bipolar-Stepper-5-7oz/dp/B00PLIW946 | 23.95 | 23.95 | Spins metal rod
1 | 4mm to 8mm Shaft Coupling | Amazon | https://www.amazon.com/dp/B06X9W8DNM?th=1 | 6.57 | 6.57 | Coupler to spin metal rod
3 | 0.22-inch acrylic (18"x24") | Lowe's | 239981 | 19.97 | 59.91 | 3 sheets of 18x24" or equivalent needed for the powder handling module
1 | Set of 3D printed/laser cut parts | OpenSLS github | https://github.com/MillerLabFTW/OpenSLS | 0.00 | 0.00
4 | Hardened Precision Metric Steel Shaft, 8 mm Diameter, 400 mm Length | McMaster | 6112K45 | 12.12 | 48.48 | Cut down to size for the distributor rails, the piston rails, and the spinning distributor. Distributor rails: 2x 31.5cm; piston rails: 4x 17.5cm, distributor: 20cm(?) Sand/Dremel the metal for the spinning distributor so that less powder sticks!
2 | Threaded rod NEMA 17 Tr8*8 Acme Leadscrew (320mm length) | RobotDigg | Custom order |  | 93.00 | For linear motion of distributor
1 | Threaded rod NEMA 17 Tr8*8 Acme Leadscrew (150mm length) | RobotDigg | http://www.robotdigg.com/product/100/150mm-Tr8*8-Acme-Leadscrew-Threaded-Nema17-Stepper | 30.00 | 30.00 | For linear motion of build platform
1 | RB-150AM Dual Output Shaft Servo motor | Amazon | https://www.amazon.com/RB-150AM-Output-Shaft-Servo-motor/dp/B01DT2WP6M?s=industrial | 32.66 | 32.66 | Adjustable plow position motor
4 | LM8UU Linear Bearing | RobotDigg | LM8UU | 1.90 | 7.60 | Bearings for linear motion of plow along rails
2 | 608zz bearings | RobotDigg | 608ZZ | 0.30 | 0.60 | Bearings for rotation of the spinning distributor rod
2 | Stainless Steel Ball Bearing Double Sealed, for 8 mm Shaft Diameter, 22 mm OD | McMaster | 6153K71 | 13.54 | 27.08 | Bearings rotate with the leadscrews used for distributor motion
2 | Sintered Bronze Bushing Bearing Sleeve 8mm Bore x 12mm OD x 15mm (2 pcs) | Amazon | https://www.amazon.com/Sintered-Bronze-Bushing-Bearing-Sleeve/dp/B00VG3RMZQ | 6.75 | 13.50 | Bushings for linear motion of build platform
1 | M3 x 0.5 mm Thread, 16 mm Long Zinc-Aluminum-Coated Alloy Steel Socket Head Screw | McMaster | 91274A107 | 6.15 | 6.15
1 | M3 x 0.5 mm Thread, 10 mm Long Zinc-Aluminum-Coated Alloy Steel Socket Head Screw | McMaster | 91274A105 | 5.43 | 5.43
2 | Metric Plain Steel Hex Nut, Class 6, M3 Size, .5MM Pitch, 5.5MM W, 2.4MM H, packs of 100 | McMaster | 90592A009 | 1.04 | 2.08
1 | Type 18-8 Stainless Steel Flat-Head Socket Cap Screw, M4 Size, 12mm Length, .70mm Pitch | McMaster | 92125A192 | 7.58 | 7.58
1 | Medium-Strength, Class 8, M4 x 0.7 mm Thread, Steel Hex Nut | McMaster | 90592A090 | 1.32 | 1.32
1 | Metric Compression Spring, Music Wire, 9.4 mm Overall, 5.50 mm OD, .5 mm Wire, Packs of 5 | McMaster | 94125K422 | 10.36 | 10.36
1 | Lab Scoop Spatula (Pick Scoop) 6.5" Length, Stainless Steel, Pack of 6 | Amazon | https://www.amazon.com/dp/B00BLS7FNK?psc=1 | 9.22 | 9.22 | Used as plow
8 | #4 Hose clamps (1/2-1-1/4") | Home Depot | 202309385 | 0.98 | 7.84 | To clamp steel piston rails onto motor
 |  |  |  | Components | $1135.67
 |  |  |  | + Laser cutter | $7499.00
 | Additional Recommended Materials
1 | American Educational 3070-6 Screen Sieves Set (6 Piece Set) | Amazon | http://www.amazon.com/American-Educational-3070-6-Screen-Sieves/dp/B007F19094 | 74.57 | 74.57 | Very useful for size-separating starting materials
1 | 3M 8511 Particulate Sanding N95 Respirator with Valve, 10-Pack | Amazon | http://www.amazon.com/3M-8511-Particulate-Respirator-10-Pack/dp/B0002YKBV2 | 16.44 | 16.44 | Respiratory protective equipment is critical for handling very fine powders!
1 | Laser Safety Glasses, Clear Lenses, 93% Visible Light Transmission | Thorlabs.com | LG6 | 147.90 | 147.90 | Never operate laser without appropriate eye protection
1 | Capri Tools 00308 Brush Paint Stain Varnish Set with Wood Handles, 5-Piece | Amazon | http://www.amazon.com/gp/r.html?R=3AVON5P2ZFZTG&C=3T5MUR8F9569O&H=7YSPA7UELKA2KDERBKMH7ZGEBQAA&T=C | 5.65 | 5.65 | Recommend brushes for clearing powder from build platform
1 | XL Blue Painters Tape - 7" wide x 100' long | Amazon | https://www.amazon.com/Blue-Painters-Tape-practically-platforms/dp/B00L4RCTDE | 29.95 | 29.95

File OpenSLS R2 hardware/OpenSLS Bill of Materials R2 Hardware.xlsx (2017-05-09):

MillerLab OpenSLS Bill of Materials R2 Hardware
Quantity | Piston? | Item | Vendor | Part No | Cost Per Item ($) | Total Cost ($) | Notes
1 |  | 80 Watt CO2 Laser Cutter 600x900mm | SeeMeCNC.com |  | 7499.00 | 7499.00 | Any stepper motor-driver laser cutter should be suitable. We purchased an 80W laser cutter but swapped the 80W tube/power supply for a 40W.
1 |  | 40W PWM CO2 Laser Power Supply | LightObject.com | LSR-JN40W3VPWM | 205.00 | 205.00 | To replace the original 80W laser tube. No specific laser tube is required for OpenSLS. Use extreme caution if replacing a laser tube and read up on safety beforehand (http://www.repairfaq.org/sam/lasersaf.htm)
1 |  | 40W CO2 Sealed Laser Tube (850mm) | AutomationtechnologiesInc.com | LSR-JLD40WCO2 | 169.00 | 169.00
1 |  | High quality 18mm ZnSe Focus lens (F38.1mm) | LightObject.com | http://www.automationtechnologiesinc.com/products-page/laser-engraving/40w-laser-tube-for-the-laser-engraver | 52.00 | 52.00
1 |  | RAMBo | Ultimachine | UMRAMBOPAC13 | 170.00 | 170.00
4 |  | NEMA17 Stepper Motor 40mm Long, 1.2A | RobotDigg.com | http://www.robotdigg.com/product/7/NEMA17-Stepper-Motor-40mm-Long,-1.2A | 6.80 | 27.20
1 |  | 12V 30A PSU | http://www.amazon.com/360w-Regulated-Switching-Power-Supply/dp/B0089VIBL2 |  | 25.65 | 25.65
50 |  | 18 AWG Power Wire (by the foot) | http://www.superbrightleds.com/moreinfo/led-vehicle-replacement-bulbs/18-awg-two-conductor-power-wire/535/ | WP18-2 | 0.19 | 9.50
50 |  | 14 AWG Power Wire (by the foot) | http://www.superbrightleds.com/moreinfo/led-vehicle-replacement-bulbs/14-awg-two-conductor-power-wire/775/ | WDRB14-2 | 0.49 | 24.50
2 |  | 2.54mm 1x4 Connector & Housing Kit - 5 pack | Ultimachine | UM1X4CBCN | 3.00 | 6.00
1 |  | Pluggable Terminal Block, 4 contacts | Ultimachine | UMTBLK4PLUG | 3.30 | 3.30
2 |  | Clear acrylic sheet 1/4" thickness | Inventables.com | 23876-17 | 29.31 | 58.62 | 1/4" acrylic for the powder module outer walls
2 |  | Clear acrylic sheet 1/8" thickness | Inventables.com | 23876-12 | 15.25 | 30.50 | 1/8" acrylic for the excess powder ducting and powder module top plate
1 |  | Set of 3D printed parts | OpenSLS github | https://github.com/MillerLabFTW/OpenSLS | 0.00 | 0.00
3 | Acrylic | Hardened Precision Metric Steel Shaft, 8 mm Diameter, 400 mm Length | McMaster | 6112K45 | 12.12 | 36.36 | Needed for both the distributor rails and the acrylic piston
1 | Acrylic | Metric Class 4.6 Plain Steel Threaded Rod, M8 Size, 300MM Length, 1.00MM Pitch, Fine Thread | McMaster | 98861A525 | 11.00 | 11.00 | Threaded rod leadscrew for piston motion, match to the pitch of your M8 nut
2 | Aluminum | Low-Carbon Steel Sheet, 1/16" Thick, 3" X 3", Ground Finish | McMaster | 1388K142 | 7.11 | 14.22
1 | Aluminum | KR2001A+200L0-0000 Linear Actuator | THK or Technico, Inc | http://www.technico.com/product/kr2001a200l0-0000/ | 710.00 | 710.00
1 | Aluminum | EXTRUDED ALUMINUM SQUARE TUBE | Onlinemetals.com | 6061 T6 | 3.19 | 3.19
1 | Aluminum | Aluminum Floor-Mounting Bracket, 5" Long for Aluminum Bolt-Together Framing | McMaster | 8809T64 | 14.79 | 14.79
1 |  | Hardened Precision Metric Steel Shaft, 5 mm Diameter, 200 mm Length | McMaster | 6112K37 | 9.02 | 9.02 | Cut to 167mm to serve as axle for distributor pulleys (non-motor side)
1 | Aluminum | Steel Perforated Sheet, .05" Hole Diameter, 26% Open, 22 Gauge, .03" Thick 24"x24" | McMaster | 9255T31 | 25.34 | 25.34 | Platform in aluminum piston design
1 |  | Metric Class 12.9 Socket Head Cap Screw, Alloy Steel, M2.5 Thread, 12MM Length, 0.45MM Pitch, packs of 100 | McMaster | 91290A104 | 13.80 | 13.80
1 |  | Metric Plain Steel Hex Nut, Class 6, M2.5 Size, .45 mm Pitch, 5MM W, 2MM H, packs of 100 | McMaster | 90592A006 | 1.04 | 1.04
1 |  | Metric DIN 125 18-8 Stainless Steel Flat Washer, M2.5 Screw Size, 6MM OD, 0.45MM-0.55MM Thick, packs of 100 | McMaster | 93475A196 | 1.58 | 1.58
1 |  | Metric 18-8 Stainless Steel Flat Head Socket Cap Screw, M3 Size, 10MM Length, .50MM Pitch, packs of 100 | McMaster | 92125A130 | 5.81 | 5.81
1 |  | Metric Plain Steel Hex Nut, Class 6, M3 Size, .5MM Pitch, 5.5MM W, 2.4MM H, packs of 100 | McMaster | 90592A009 | 1.04 | 1.04
1 | Acrylic | Zinc Plated Steel Hex Nut, Class 8, M8x1.25 Thread Size, 13mm Wide, 6.5mm High , pack of 100 | McMaster | 90690A055 | 5.07 | 5.07 | Slips inside 3D printed part to anchor the acrylic piston leadscrew. Make sure the pitch matches the pitch of M8 threaded rods
1 |  | Type 18-8 Stainless Steel Flat-Head Socket Cap Screw, M4 Size, 12mm Length, .70mm Pitch | McMaster | 92125A192 | 7.58 | 7.58
4 |  | Aluminum GT2 Timing Pulley - 6mm Belt - 20 Tooth - 5mm Bore | Adafruit.com | 1251 | 7.95 | 31.80
4 |  | Timing Belt GT2 Profile - 2mm pitch - 6mm wide 1164mm long | Adafruit.com | 1184 | 9.95 | 39.80
1 |  | Metric Compression Spring, Music Wire, 9.4 mm Overall, 5.50 mm OD, .5 mm Wire, Packs of 5 | McMaster | 94125K422 | 10.36 | 10.36
1 |  | Black Oxide Steel Knurled Head Thumb Screw, Low Head, M3 Thread, 0.5MM Pitch, 10MM Long | McMaster | 92545A119 | 2.20 | 2.20
1 |  | 18-8 Stainless Steel Knurled Head Thumb Screw, Low Head, M3 Thread, 0.5MM Pitch, 11MM Long | McMaster | 92552A414 | 2.60 | 2.60
1 |  | 12 LM8UU Linear Bearings for 3D Printer. Prusa Mendel, reprap | Amazon | http://www.amazon.com/gp/r.html?R=3AVON5P2ZFZTG&C=3T5MUR8F9569O&H=A37OLVQHBQFDPJ3SMBJFS8I4KXEA&T=C | 19.50 | 19.50 | Bearings for inside distributor
1 | Acrylic | Flexible Coupler - 25772-02 | Inventables.com | 25772-02 | 6.95 | 6.95 | Connect threaded leadscrews to stepper motors
4 | Acrylic | #4 Hose clamps (1/2-1-1/4") | Home Depot | 202309385 | 0.98 | 3.92
10 | Aluminum | Metric Aluminum Unthreaded Spacer, 10MM OD, 16MM Length, M4 Screw Size | McMaster | 94669A814 | 1.42 | 14.20
4 |  | Sealed Bearing - 5mm x 16mm x 5mm - 25196-01 | Inventables.com | 25196-01 | 1.25 | 5.00
1 |  | Extra Firm White F1 Felt | McMaster | 8334K31 (http://www.mcmaster.com/) | 13.69 | 13.69 | Felt gasket between acrylic sheets creates a powder-free seal for moving pistons
1 |  | LAB SCOOP Stainless steel, 6" long 3pk | Amazon | http://www.amazon.com/SEOH-SCOOP-Stainless-steel-long/dp/B0018RUGA8 | 7.95 | 7.95 | For the distributor
 | Note on piston construction: We have developed two similar piston designs. One uses a combinaton of 3D printed parts, 8mm smooth steel rods, and 8mm threaded leadscrew with an acrylic platform and acrylic walls. The other uses a linear actuator (KR20 series) with an aluminum housing (extruded aluminm square) and a platform made of perforated steel. Our R2 hardware uses the acrylic design with smooth rods for the powder reservoir and the aluminum design with linear actuator for the build platform. The aluminum design was designed for heating the build volume, which we have not yet implemented. It is possible to build two (cheaper) acrylic pistons instead - just replace the parts marked "Aluminum" (piston column) by doubling the quantities for compenents marked "acrylic". This will require you to design and lasercut appropriate acrylic piston walls and platform.
 |  |  |  |  | Components | $1799.08
 |  |  |  |  | + Laser cutter | $7499.00
 |  |  |  |  | Grand total | $9298.08
 |  | Additional Recommended Materials
1 |  | American Educational 3070-6 Screen Sieves Set (6 Piece Set) | Amazon | http://www.amazon.com/American-Educational-3070-6-Screen-Sieves/dp/B007F19094 | 74.57 | 74.57 | Very useful for size-separating starting materials
1 |  | 3M 8511 Particulate Sanding N95 Respirator with Valve, 10-Pack | Amazon | http://www.amazon.com/3M-8511-Particulate-Respirator-10-Pack/dp/B0002YKBV2 | 16.44 | 16.44 | Respiratory protective equipment is critical for handling very fine powders!
1 |  | Laser Safety Glasses, Clear Lenses, 93% Visible Light Transmission | Thorlabs.com | LG6 | 147.90 | 147.90 | Never operate laser without appropriate eye protection
1 |  | Capri Tools 00308 Brush Paint Stain Varnish Set with Wood Handles, 5-Piece | Amazon | http://www.amazon.com/gp/r.html?R=3AVON5P2ZFZTG&C=3T5MUR8F9569O&H=7YSPA7UELKA2KDERBKMH7ZGEBQAA&T=C | 5.65 | 5.65 | Recommend brushes for clearing powder from build platform

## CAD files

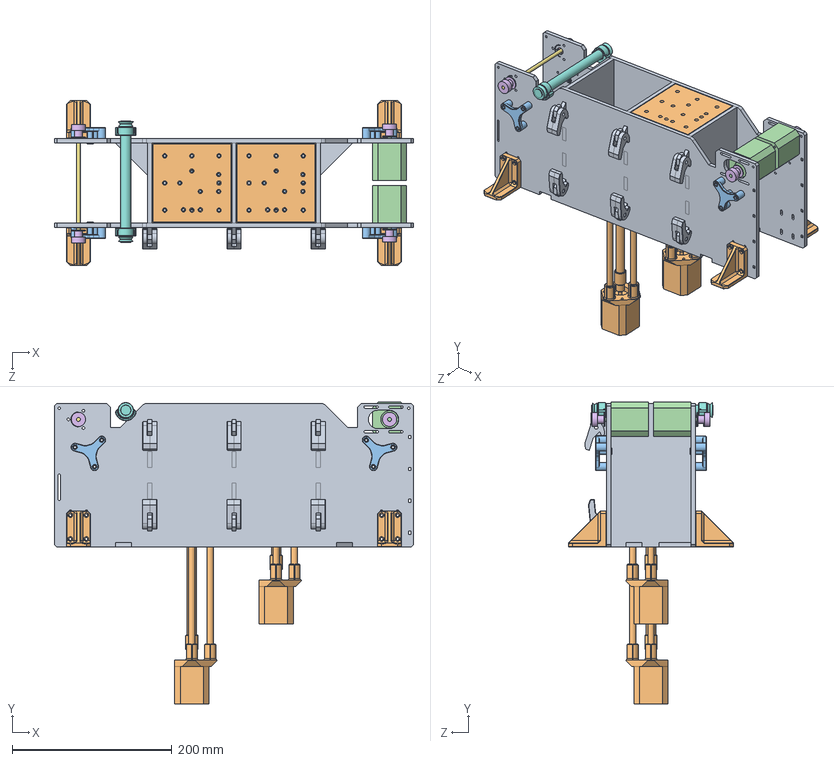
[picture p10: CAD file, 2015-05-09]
OpenSLS R1 hardware/OpenSLS r1 Assembly.SLDASM
450.0 x 378.0 x 207.2 mm
body r1
piston x 2
idler mount x 4
kysan NEMA17 x 2
5mm bearing x 2
gt2 pulley x 4
5mmx148.5
POWDER DISTRIBUTOR
cam lock x 6
foot x 4
acme plate x 2

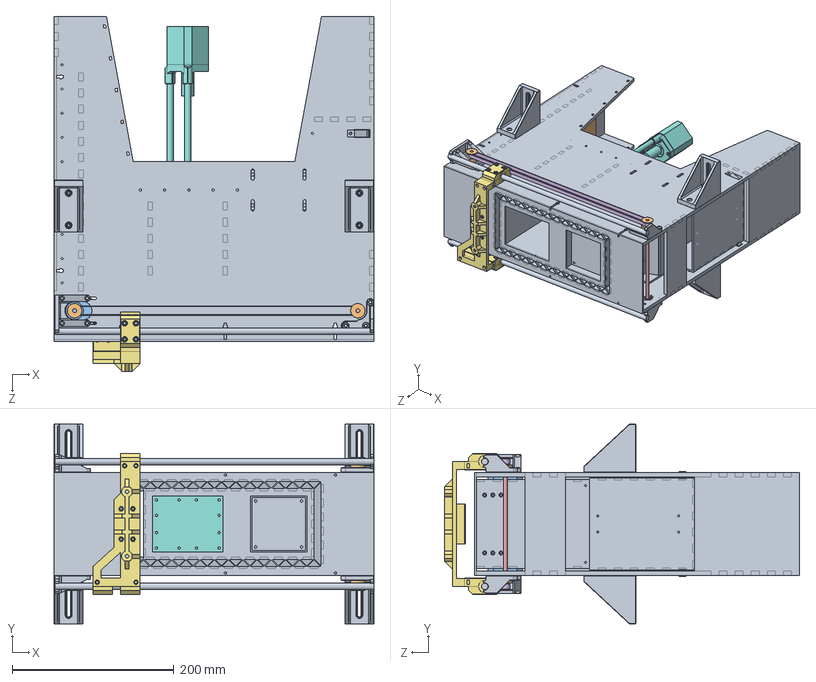
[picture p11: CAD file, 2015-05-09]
OpenSLS R2 hardware/R2 full assembly.SLDASM
396.2 x 247.4 x 440.0 mm
R2 body
gt2 pulley x 4
kysan NEMA17 x 2
5mm bearing x 2
5mm x 164.7mm
gt2 dist drive belt x 2
distributor r3
feed piston
acme plate
ATX 12V SUpply

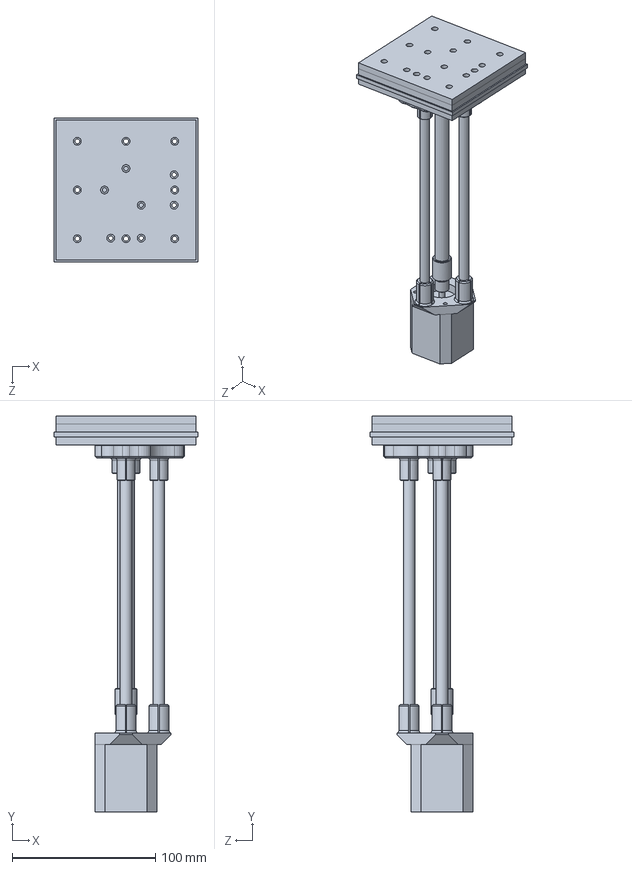
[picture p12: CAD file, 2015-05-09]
OpenSLS R1 hardware/acrylic body and pistons/pistons/piston assembly.SLDPRT
100.4 x 276.5 x 100.4 mm

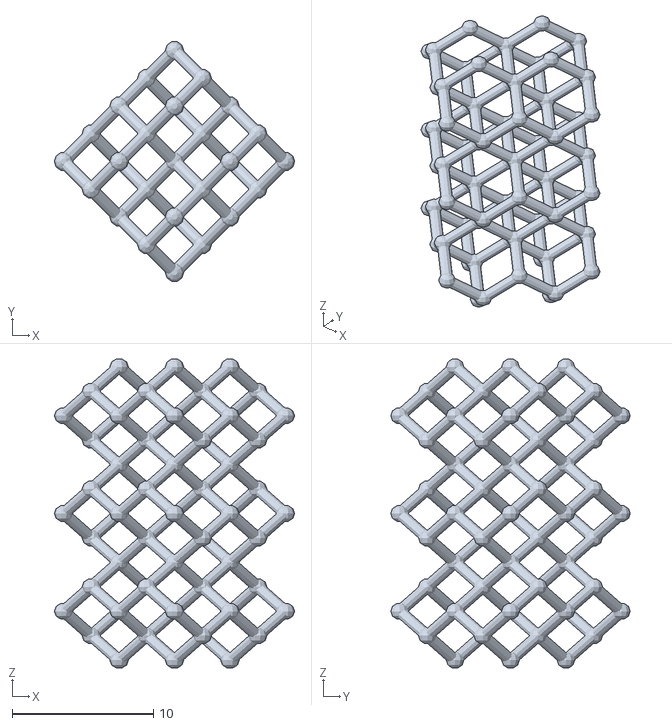
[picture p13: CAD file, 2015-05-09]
Model Geometries/Reduced_diamond_lattice.stl
17.0 x 17.0 x 21.9

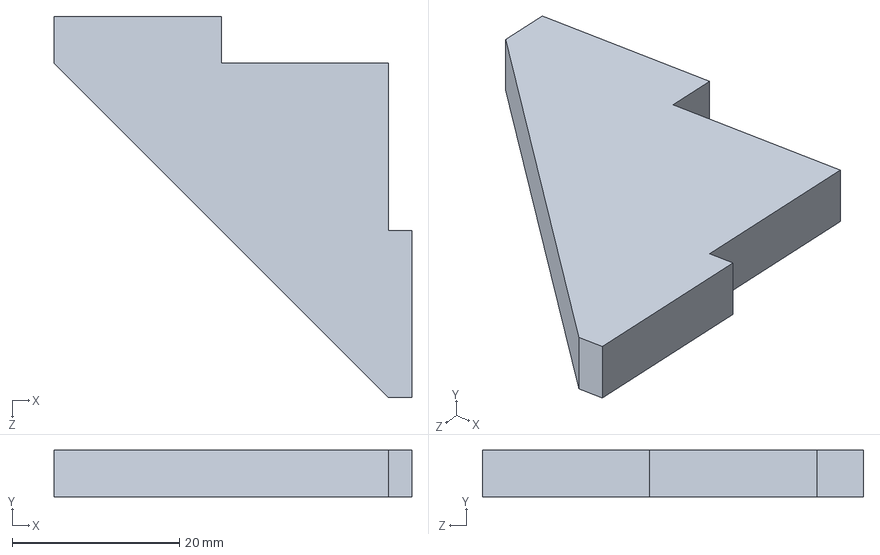
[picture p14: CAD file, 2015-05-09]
OpenSLS R1 hardware/acrylic body and pistons/corner brace B.SLDPRT
42.8 x 5.60 x 45.6 mm

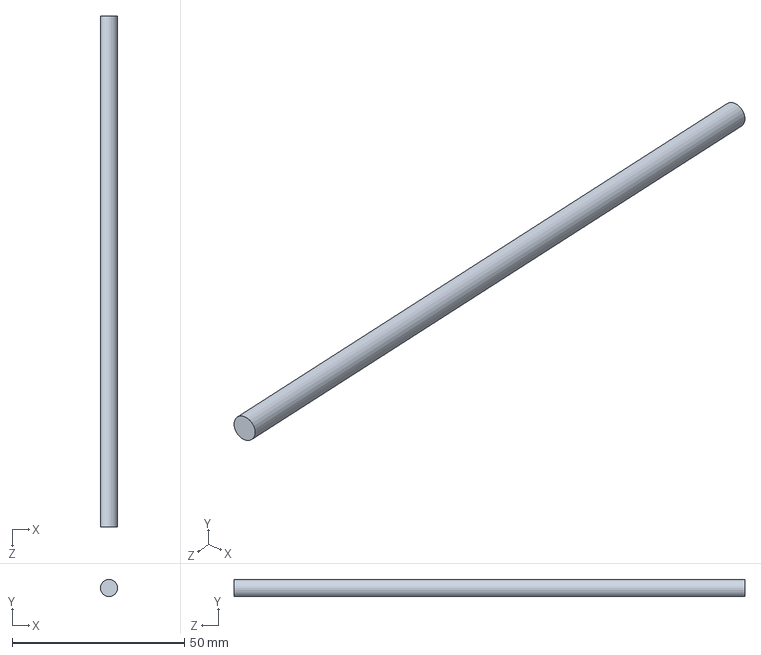
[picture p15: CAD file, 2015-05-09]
OpenSLS R1 hardware/acrylic body and pistons/misc hardware/5mmx148.5.SLDPRT
5.00 x 5.00 x 148.5 mm

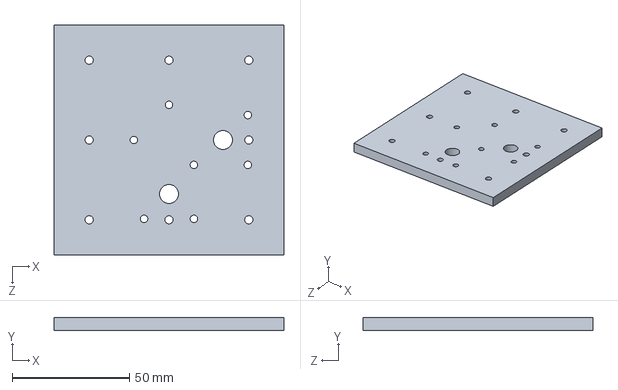
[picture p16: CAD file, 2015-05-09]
OpenSLS R1 hardware/acrylic body and pistons/pistons/gasket clamp plate.SLDPRT
98.0 x 5.60 x 98.0 mm

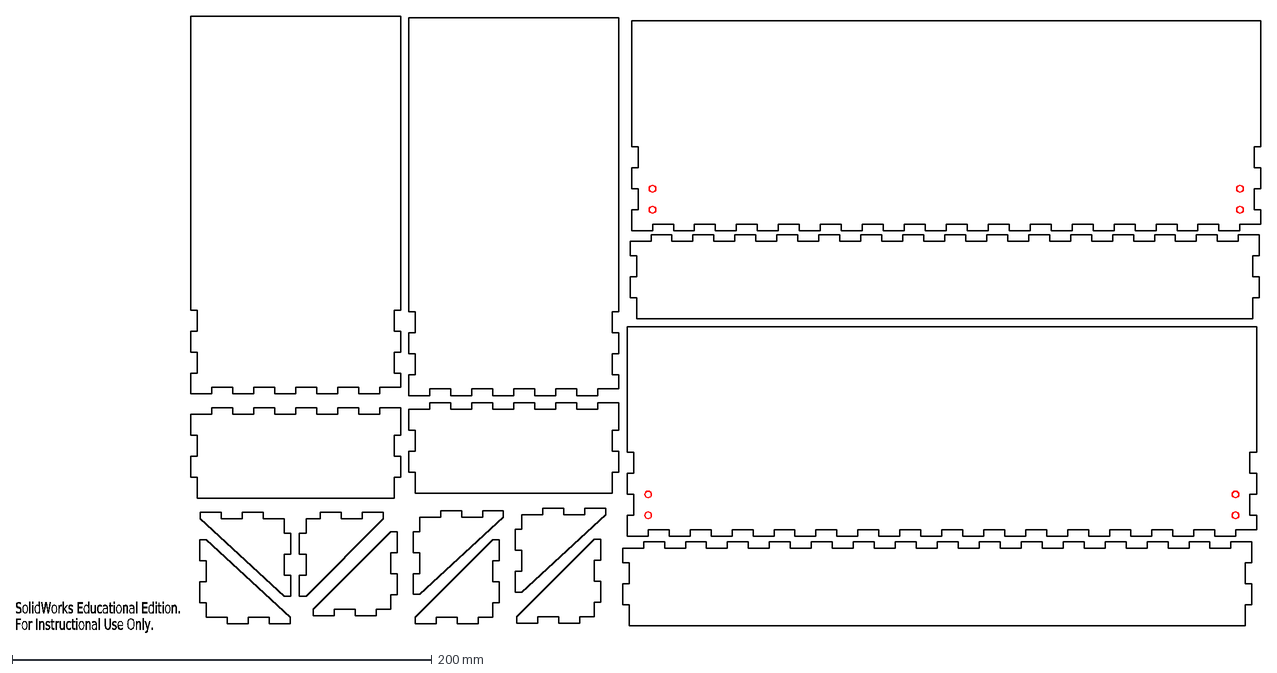
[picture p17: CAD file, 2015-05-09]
OpenSLS R1 hardware/powder capture troughs and stand/Laser Cutting/powder catchers.DXF
SolidWorks Educational Edition.
For Instructional Use Only.

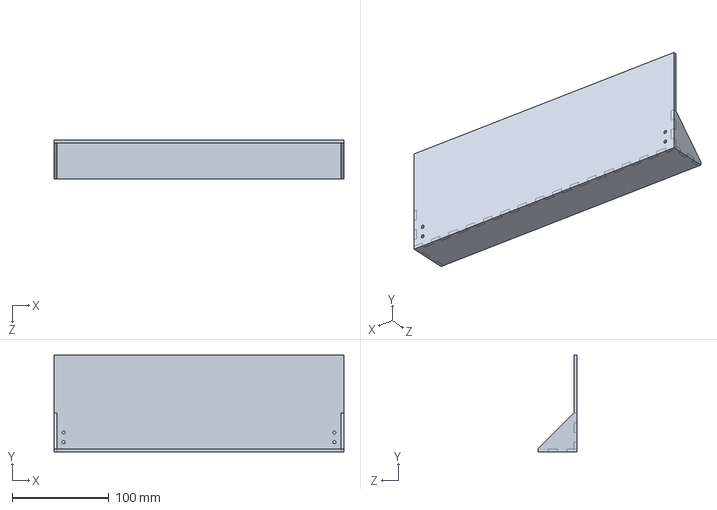
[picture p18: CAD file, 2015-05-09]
OpenSLS R1 hardware/powder capture troughs and stand/long wall trough/powderCather2.SLDPRT
300.0 x 100.0 x 40.0 mm

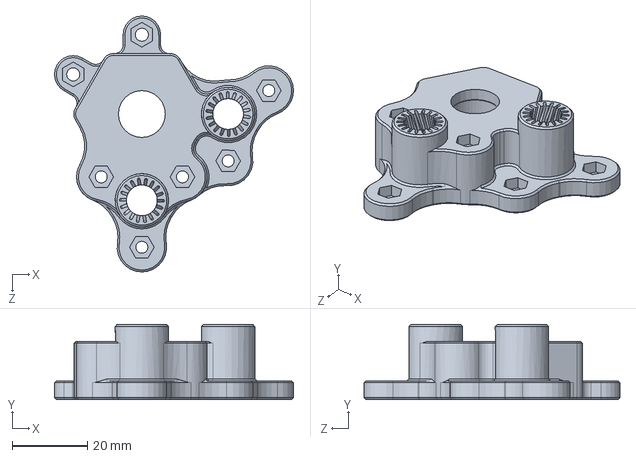
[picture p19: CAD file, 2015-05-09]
OpenSLS R1 hardware/printed parts/acme plate.SLDPRT
63.7 x 20.0 x 68.2 mm

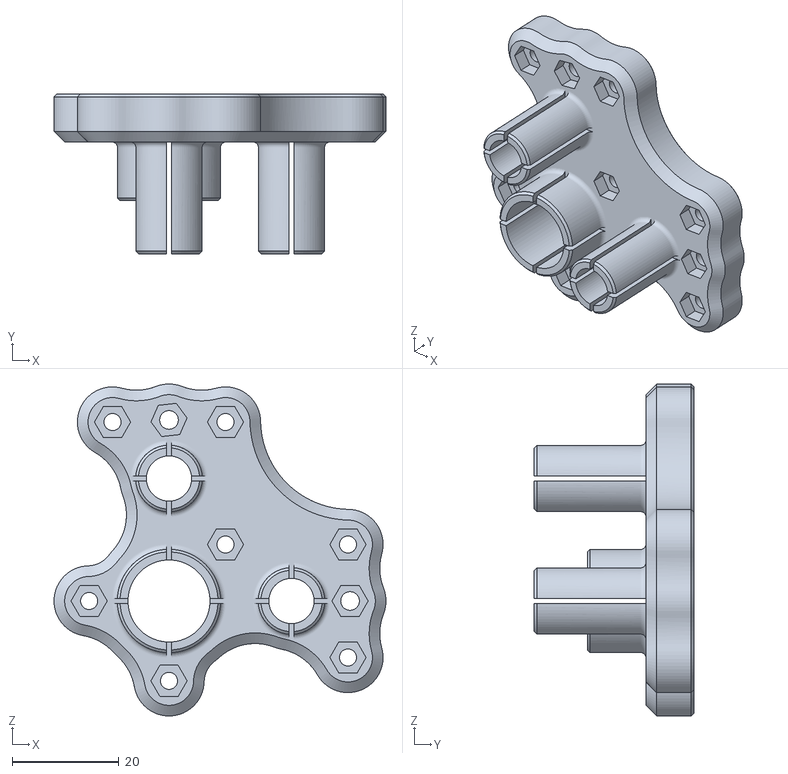
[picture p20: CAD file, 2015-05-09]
OpenSLS R1 hardware/STLs/pistonHeadMount.STL
62.3 x 30.0 x 62.3

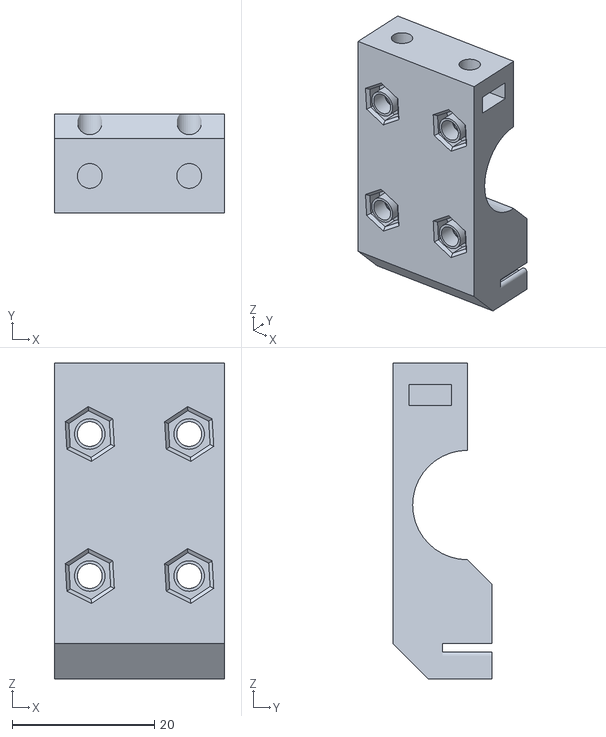
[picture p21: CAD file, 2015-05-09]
OpenSLS R2 hardware/Distributor/distributor r3-Belt block 1.STL
24.0 x 14.0 x 44.5

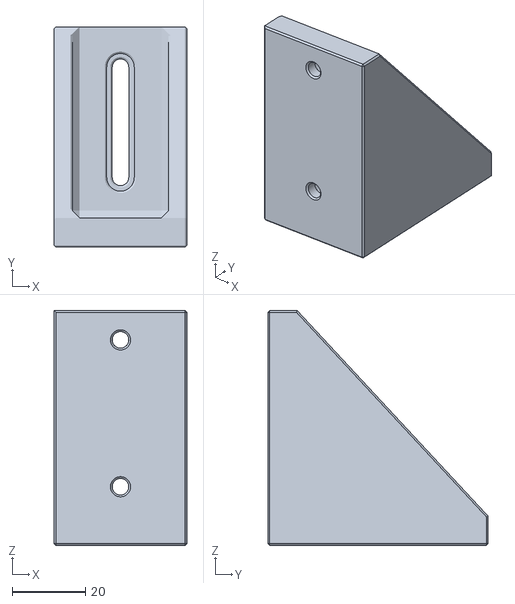
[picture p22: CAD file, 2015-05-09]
OpenSLS R2 hardware/Fabrication Files/3D Printed Parts/integration bracket.STL
36.2 x 60.0 x 64.0

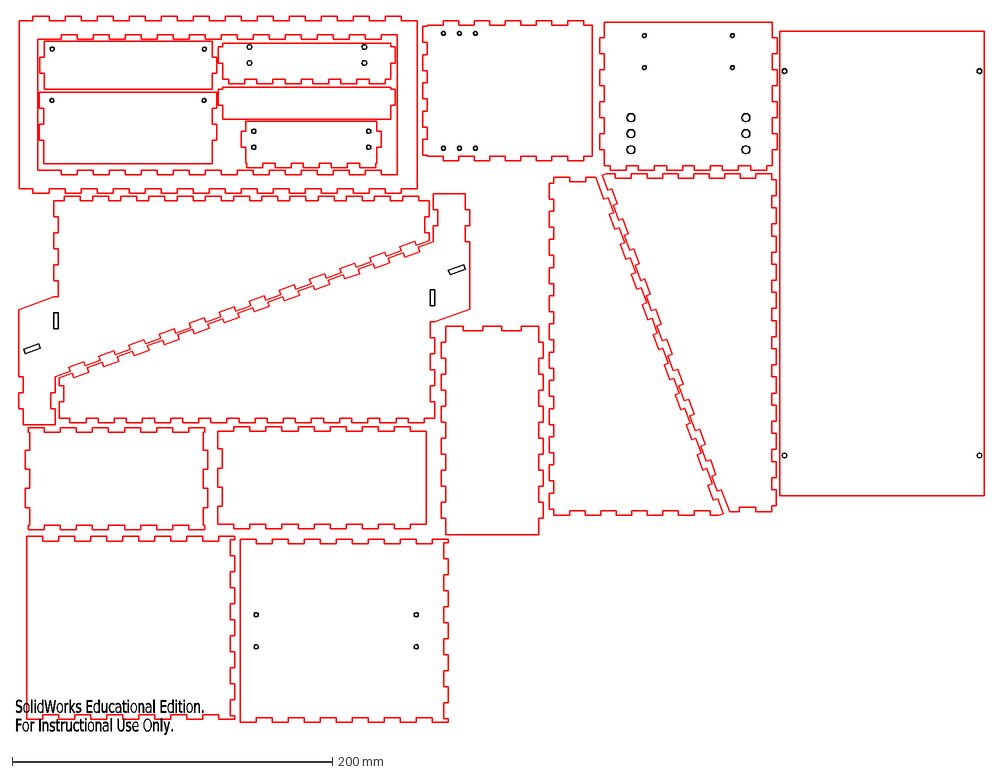
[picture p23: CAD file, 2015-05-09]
OpenSLS R2 hardware/Fabrication Files/Laser Cutting/2.83mm Acrylic/2.83mm Acrylic Parts.DXF
SolidWorks Educational Edition.
For Instructional Use Only.

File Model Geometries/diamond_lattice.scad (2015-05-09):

/*

Creates a model of a molcule from a set
of orthogonal coordinates  here part of diamond lattice

*/

module atom(rx,x0,y0,z0)
{
  translate(v=[x0,y0,z0])
  sphere(r=rx,$fn=10);
}

/* spheres of radius rx are placed at the atomic
 positions - x0,y0,z0
*/



module bond(x2,y2,z2,x1,y1,z1)

{
tx = (x2 + x1)/2;
ty = (y2 + y1)/2;
tz = (z2 + z1)/2;
ax = x2 - x1 ;
ay = y2 - y1;
az = z2 - z1;

translate(v=[tx,ty,tz])
rotate(a = [-acos(az/sqrt(ax*ax+ay*ay+az*az)), 0, -atan2(ax, ay)])
cylinder(r=.3,h=sqrt(ax*ax+ay*ay+az*az),center=true,$fn=10);
}

/*

Module bond represents a bond between two atoms -
as a cylinder - the orthogonal coordinates of the two
atoms are passed


tx,ty,and tz are the coordinates of the midpoint of the line
             connecting the atoms
ax,ay,and az is the vector between the atoms

              A cylinder whose height is equal to the bond length
              is placed at the origin and rotated to align with the
              bond.  The cylinder is then translated to the proper
              position

             David Moews supplied the rotate command.

                                                            P Moews


*/

 /*  comment out 4 atoms and 4 bonds which slant downward
     82 90 100 slant downward 82 on the raft?
     196 202 212 slant downward  196 on the raft?
     structure should be properly oriented - move up to build
     platform to print
*/

union()
{

atom(.5,  0.449250, -3.120750, -3.120750);  //   1
atom(.5, -1.335750, -1.335750, -3.120750);  //   3
atom(.5,  0.449250,  0.449250, -3.120750);  //   4
atom(.5, -1.335750, -3.120750, -1.335750);  //   5
atom(.5,  0.449250, -1.335750, -1.335750);  //   6
atom(.5, -0.443250, -2.228250, -2.228250);  //   7
atom(.5,  0.449250, -3.120750,  0.449250);  //   8
atom(.5, -3.120750,  0.449250, -3.120750);  //   9
atom(.5, -3.120750, -1.335750, -1.335750);  //  10
atom(.5, -1.335750,  0.449250, -1.335750);  //  11
atom(.5, -2.228250, -0.443250, -2.228250);  //  12
atom(.5, -3.120750, -3.120750,  0.449250);  //  13
atom(.5, -1.335750, -1.335750,  0.449250);  //  14
atom(.5, -2.228250, -2.228250, -0.443250);  //  15
atom(.5,  0.449250,  0.449250,  0.449250);  //  16
atom(.5, -0.443250, -0.443250, -0.443250);  //  17
atom(.5, -3.120750,  0.449250,  0.449250);  //  18
atom(.5, -1.335750, -3.120750,  2.231250);  //  19
atom(.5,  0.449250, -1.335750,  2.231250);  //  20
atom(.5, -0.443250, -2.228250,  1.338750);  //  21
atom(.5,  0.449250, -3.120750,  4.016250);  //  22
atom(.5, -3.120750, -1.335750,  2.231250);  //  23
atom(.5, -1.335750,  0.449250,  2.231250);  //  24
atom(.5, -2.228250, -0.443250,  1.338750);  //  25
atom(.5, -3.120750, -3.120750,  4.016250);  //  26
atom(.5, -1.335750, -1.335750,  4.016250);  //  27
atom(.5, -2.228250, -2.228250,  3.123750);  //  28
atom(.5,  0.449250,  0.449250,  4.016250);  //  29
atom(.5, -0.443250, -0.443250,  3.123750);  //  30
atom(.5, -3.120750,  0.449250,  4.016250);  //  31
atom(.5, -1.335750, -3.120750,  5.798250);  //  32
atom(.5,  0.449250, -1.335750,  5.798250);  //  33
atom(.5, -0.443250, -2.228250,  4.905750);  //  34
atom(.5,  0.449250, -3.120750,  7.583250);  //  35
atom(.5, -3.120750, -1.335750,  5.798250);  //  36
atom(.5, -1.335750,  0.449250,  5.798250);  //  37
atom(.5, -2.228250, -0.443250,  4.905750);  //  38
atom(.5, -3.120750, -3.120750,  7.583250);  //  39
atom(.5, -1.335750, -1.335750,  7.583250);  //  40
atom(.5, -2.228250, -2.228250,  6.690750);  //  41
atom(.5,  0.449250,  0.449250,  7.583250);  //  42
atom(.5, -0.443250, -0.443250,  6.690750);  //  43
atom(.5, -3.120750,  0.449250,  7.583250);  //  44
atom(.5, -1.335750,  2.231250, -3.120750);  //  45
atom(.5,  0.449250,  4.016250, -3.120750);  //  46
atom(.5,  0.449250,  2.231250, -1.335750);  //  47
atom(.5, -0.443250,  1.338750, -2.228250);  //  48
atom(.5, -3.120750,  4.016250, -3.120750);  //  49
atom(.5, -3.120750,  2.231250, -1.335750);  //  50
atom(.5, -1.335750,  4.016250, -1.335750);  //  51
atom(.5, -2.228250,  3.123750, -2.228250);  //  52
atom(.5, -1.335750,  2.231250,  0.449250);  //  53
atom(.5, -2.228250,  1.338750, -0.443250);  //  54
atom(.5,  0.449250,  4.016250,  0.449250);  //  55
atom(.5, -0.443250,  3.123750, -0.443250);  //  56
atom(.5, -3.120750,  4.016250,  0.449250);  //  57
atom(.5,  0.449250,  2.231250,  2.231250);  //  58
atom(.5, -0.443250,  1.338750,  1.338750);  //  59
atom(.5, -3.120750,  2.231250,  2.231250);  //  60
atom(.5, -1.335750,  4.016250,  2.231250);  //  61
atom(.5, -2.228250,  3.123750,  1.338750);  //  62
atom(.5, -1.335750,  2.231250,  4.016250);  //  63
atom(.5, -2.228250,  1.338750,  3.123750);  //  64
atom(.5,  0.449250,  4.016250,  4.016250);  //  65
atom(.5, -0.443250,  3.123750,  3.123750);  //  66
atom(.5, -3.120750,  4.016250,  4.016250);  //  67
atom(.5,  0.449250,  2.231250,  5.798250);  //  68
atom(.5, -0.443250,  1.338750,  4.905750);  //  69
atom(.5, -3.120750,  2.231250,  5.798250);  //  70
atom(.5, -1.335750,  4.016250,  5.798250);  //  71
atom(.5, -2.228250,  3.123750,  4.905750);  //  72
atom(.5, -1.335750,  2.231250,  7.583250);  //  73
atom(.5, -2.228250,  1.338750,  6.690750);  //  74
atom(.5,  0.449250,  4.016250,  7.583250);  //  75
atom(.5, -0.443250,  3.123750,  6.690750);  //  76
atom(.5, -3.120750,  4.016250,  7.583250);  //  77
atom(.5, -1.335750,  5.798250, -3.120750);  //  78
atom(.5,  0.449250,  7.583250, -3.120750);  //  79
atom(.5,  0.449250,  5.798250, -1.335750);  //  80
atom(.5, -0.443250,  4.905750, -2.228250);  //  81
atom(.5, -3.120750,  7.583250, -3.120750);  //  82
atom(.5, -3.120750,  5.798250, -1.335750);  //  83
atom(.5, -1.335750,  7.583250, -1.335750);  //  84
atom(.5, -2.228250,  6.690750, -2.228250);  //  85
atom(.5, -1.335750,  5.798250,  0.449250);  //  86
atom(.5, -2.228250,  4.905750, -0.443250);  //  87
atom(.5,  0.449250,  7.583250,  0.449250);  //  88
atom(.5, -0.443250,  6.690750, -0.443250);  //  89
//atom(.5, -3.120750,  7.583250,  0.449250);  //  90
atom(.5,  0.449250,  5.798250,  2.231250);  //  91
atom(.5, -0.443250,  4.905750,  1.338750);  //  92
atom(.5, -3.120750,  5.798250,  2.231250);  //  93
atom(.5, -1.335750,  7.583250,  2.231250);  //  94
atom(.5, -2.228250,  6.690750,  1.338750);  //  95
atom(.5, -1.335750,  5.798250,  4.016250);  //  96
atom(.5, -2.228250,  4.905750,  3.123750);  //  97
atom(.5,  0.449250,  7.583250,  4.016250);  //  98
atom(.5, -0.443250,  6.690750,  3.123750);  //  99
//atom(.5, -3.120750,  7.583250,  4.016250);  // 100
atom(.5,  0.449250,  5.798250,  5.798250);  // 101
atom(.5, -0.443250,  4.905750,  4.905750);  // 102
atom(.5, -3.120750,  5.798250,  5.798250);  // 103
atom(.5, -1.335750,  7.583250,  5.798250);  // 104
atom(.5, -2.228250,  6.690750,  4.905750);  // 105
atom(.5, -1.335750,  5.798250,  7.583250);  // 106
atom(.5, -2.228250,  4.905750,  6.690750);  // 107
atom(.5,  0.449250,  7.583250,  7.583250);  // 108
atom(.5, -0.443250,  6.690750,  6.690750);  // 109
atom(.5,  4.016250, -3.120750, -3.120750);  // 111
atom(.5,  2.231250, -1.335750, -3.120750);  // 112
atom(.5,  4.016250,  0.449250, -3.120750);  // 113
atom(.5,  2.231250, -3.120750, -1.335750);  // 114
atom(.5,  4.016250, -1.335750, -1.335750);  // 115
atom(.5,  3.123750, -2.228250, -2.228250);  // 116
atom(.5,  4.016250, -3.120750,  0.449250);  // 117
atom(.5,  2.231250,  0.449250, -1.335750);  // 118
atom(.5,  1.338750, -0.443250, -2.228250);  // 119
atom(.5,  2.231250, -1.335750,  0.449250);  // 120
atom(.5,  1.338750, -2.228250, -0.443250);  // 121
atom(.5,  4.016250,  0.449250,  0.449250);  // 122
atom(.5,  3.123750, -0.443250, -0.443250);  // 123
atom(.5,  2.231250, -3.120750,  2.231250);  // 124
atom(.5,  4.016250, -1.335750,  2.231250);  // 125
atom(.5,  3.123750, -2.228250,  1.338750);  // 126
atom(.5,  4.016250, -3.120750,  4.016250);  // 127
atom(.5,  2.231250,  0.449250,  2.231250);  // 128
atom(.5,  1.338750, -0.443250,  1.338750);  // 129
atom(.5,  2.231250, -1.335750,  4.016250);  // 130
atom(.5,  1.338750, -2.228250,  3.123750);  // 131
atom(.5,  4.016250,  0.449250,  4.016250);  // 132
atom(.5,  3.123750, -0.443250,  3.123750);  // 133
atom(.5,  2.231250, -3.120750,  5.798250);  // 134
atom(.5,  4.016250, -1.335750,  5.798250);  // 135
atom(.5,  3.123750, -2.228250,  4.905750);  // 136
atom(.5,  4.016250, -3.120750,  7.583250);  // 137
atom(.5,  2.231250,  0.449250,  5.798250);  // 138
atom(.5,  1.338750, -0.443250,  4.905750);  // 139
atom(.5,  2.231250, -1.335750,  7.583250);  // 140
atom(.5,  1.338750, -2.228250,  6.690750);  // 141
atom(.5,  4.016250,  0.449250,  7.583250);  // 142
atom(.5,  3.123750, -0.443250,  6.690750);  // 143
atom(.5,  2.231250,  2.231250, -3.120750);  // 144
atom(.5,  4.016250,  4.016250, -3.120750);  // 145
atom(.5,  4.016250,  2.231250, -1.335750);  // 146
atom(.5,  3.123750,  1.338750, -2.228250);  // 147
atom(.5,  2.231250,  4.016250, -1.335750);  // 148
atom(.5,  1.338750,  3.123750, -2.228250);  // 149
atom(.5,  2.231250,  2.231250,  0.449250);  // 150
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

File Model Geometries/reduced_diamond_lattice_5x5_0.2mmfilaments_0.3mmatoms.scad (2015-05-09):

/*

Creates a model of a molcule from a set
of orthogonal coordinates  here part of diamond lattice

*/

module atom(rx,x0,y0,z0)
{
  translate(v=[x0,y0,z0])
  sphere(r=rx,$fn=10);
}

/* spheres of radius rx are placed at the atomic
 positions - x0,y0,z0
*/



module bond(x2,y2,z2,x1,y1,z1)

{
tx = (x2 + x1)/2;
ty = (y2 + y1)/2;
tz = (z2 + z1)/2;
ax = x2 - x1 ;
ay = y2 - y1;
az = z2 - z1;

translate(v=[tx,ty,tz])
rotate(a = [-acos(az/sqrt(ax*ax+ay*ay+az*az)), 0, -atan2(ax, ay)])
cylinder(r=.2,h=sqrt(ax*ax+ay*ay+az*az),center=true,$fn=10);
}

/*

Module bond represents a bond between two atoms -
as a cylinder - the orthogonal coordinates of the two
atoms are passed


tx,ty,and tz are the coordinates of the midpoint of the line
             connecting the atoms
ax,ay,and az is the vector between the atoms

              A cylinder whose height is equal to the bond length
              is placed at the origin and rotated to align with the
              bond.  The cylinder is then translated to the proper
              position

             David Moews supplied the rotate command.

                                                            P Moews


*/

 /*  comment out 4 atoms and 4 bonds which slant downward
     82 90 100 slant downward 82 on the raft?
     196 202 212 slant downward  196 on the raft?
     structure should be properly oriented - move up to build
     platform to print
*/

union()
{

//atom(.3,  0.449250, -3.120750, -3.120750);  //   1
//atom(.3, -1.335750, -1.335750, -3.120750);  //   3
atom(.3,  0.449250,  0.449250, -3.120750);  //   4
//atom(.3, -1.335750, -3.120750, -1.335750);  //   5
atom(.3,  0.449250, -1.335750, -1.335750);  //   6
//atom(.3, -0.443250, -2.228250, -2.228250);  //   
//atom(.3,  0.449250, -3.120750,  0.449250);  //   8
//atom(.3, -3.120750,  0.449250, -3.120750);  //   9
//atom(.3, -3.120750, -1.335750, -1.335750);  //  10
atom(.3, -1.335750,  0.449250, -1.335750);  //  11
//atom(.3, -2.228250, -0.443250, -2.228250);  //  12
//atom(.3, -3.120750, -3.120750,  0.449250);  //  13
//atom(.3, -1.335750, -1.335750,  0.449250);  //  14
//atom(.3, -2.228250, -2.228250, -0.443250);  //  15
atom(.3,  0.449250,  0.449250,  0.449250);  //  16
atom(.3, -0.443250, -0.443250, -0.443250);  //  17
//atom(.3, -3.120750,  0.449250,  0.449250);  //  18
//atom(.3, -1.335750, -3.120750,  2.231250);  //  19
atom(.3,  0.449250, -1.335750,  2.231250);  //  20
//atom(.3, -0.443250, -2.228250,  1.338750);  //  21
//atom(.3,  0.449250, -3.120750,  4.016250);  //  22
//atom(.3, -3.120750, -1.335750,  2.231250);  //  23
atom(.3, -1.335750,  0.449250,  2.231250);  //  24
//atom(.3, -2.228250, -0.443250,  1.338750);  //  25
//atom(.3, -3.120750, -3.120750,  4.016250);  //  26
//atom(.3, -1.335750, -1.335750,  4.016250);  //  27
//atom(.3, -2.228250, -2.228250,  3.123750);  //  28
atom(.3,  0.449250,  0.449250,  4.016250);  //  29
atom(.3, -0.443250, -0.443250,  3.123750);  //  30
//atom(.3, -3.120750,  0.449250,  4.016250);  //  31
//atom(.3, -1.335750, -3.120750,  5.798250);  //  32
atom(.3,  0.449250, -1.335750,  5.798250);  //  33
//atom(.3, -0.443250, -2.228250,  4.905750);  //  34
//atom(.3,  0.449250, -3.120750,  7.583250);  //  35
//atom(.3, -3.120750, -1.335750,  5.798250);  //  36
atom(.3, -1.335750,  0.449250,  5.798250);  //  37

atom(.3,  0.449250,  0.449250,  7.583250);  //  42
atom(.3, -0.443250, -0.443250,  6.690750);  //  43
//atom(.3, -3.120750,  0.449250,  7.583250);  //  44
//atom(.3, -1.335750,  2.231250, -3.120750);  //  45
//atom(.3,  0.449250,  4.016250, -3.120750);  //  46
atom(.3,  0.449250,  2.231250, -1.335750);  //  47
atom(.3, -0.443250,  1.338750, -2.228250);  //  48

atom(.3,  0.449250,  2.231250,  2.231250);  //  58
atom(.3, -0.443250,  1.338750,  1.338750);  //  59

atom(.3,  0.449250,  2.231250,  5.798250);  //  68
atom(.3, -0.443250,  1.338750,  4.905750);  //  69

atom(.3,  2.231250, -1.335750, -3.120750);  // 112
atom(.3,  4.016250,  0.449250, -3.120750);  // 113
atom(.3,  2.231250, -3.120750, -1.335750);  // 114
atom(.3,  4.016250, -1.335750, -1.335750);  // 115
atom(.3,  3.123750, -2.228250, -2.228250);  // 116
//atom(.3,  4.016250, -3.120750,  0.449250);  // 117
atom(.3,  2.231250,  0.449250, -1.335750);  // 118
atom(.3,  1.338750, -0.443250, -2.228250);  // 119
atom(.3,  2.231250, -1.335750,  0.449250);  // 120
atom(.3,  1.338750, -2.228250, -0.443250);  // 121
atom(.3,  4.016250,  0.449250,  0.449250);  // 122
atom(.3,  3.123750, -0.443250, -0.443250);  // 123
atom(.3,  2.231250, -3.120750,  2.231250);  // 124
atom(.3,  4.016250, -1.335750,  2.231250);  // 125
atom(.3,  3.123750, -2.228250,  1.338750);  // 126
//atom(.3,  4.016250, -3.120750,  4.016250);  // 127
atom(.3,  2.231250,  0.449250,  2.231250);  // 128
atom(.3,  1.338750, -0.443250,  1.338750);  // 129
atom(.3,  2.231250, -1.335750,  4.016250);  // 130
atom(.3,  1.338750, -2.228250,  3.123750);  // 131
atom(.3,  4.016250,  0.449250,  4.016250);  // 132
atom(.3,  3.123750, -0.443250,  3.123750);  // 133
atom(.3,  2.231250, -3.120750,  5.798250);  // 134
atom(.3,  4.016250, -1.335750,  5.798250);  // 135
atom(.3,  3.123750, -2.228250,  4.905750);  // 136
//atom(.3,  4.016250, -3.120750,  7.583250);  // 137
atom(.3,  2.231250,  0.449250,  5.798250);  // 138
atom(.3,  1.338750, -0.443250,  4.905750);  // 139
atom(.3,  2.231250, -1.335750,  7.583250);  // 140
atom(.3,  1.338750, -2.228250,  6.690750);  // 141
atom(.3,  4.016250,  0.449250,  7.583250);  // 142
atom(.3,  3.123750, -0.443250,  6.690750);  // 143
atom(.3,  2.231250,  2.231250, -3.120750);  // 14
//atom(.3,  4.016250,  4.016250, -3.120750);  // 145
atom(.3,  4.016250,  2.231250, -1.335750);  // 146
atom(.3,  3.123750,  1.338750, -2.228250);  // 147
atom(.3,  2.231250,  4.016250, -1.335750);  // 148
atom(.3,  1.338750,  3.123750, -2.228250);  // 149
atom(.3,  2.231250,  2.231250,  0.449250);  // 150
atom(.3,  1.338750,  1.338750, -0.443250);  // 151
//atom(.3,  4.016250,  4.016250,  0.449250);  // 152
atom(.3,  3.123750,  3.123750, -0.443250);  // 153
atom(.3,  4.016250,  2.231250,  2.231250);  // 154
atom(.3,  3.123750,  1.338750,  1.338750);  // 155
atom(.3,  2.231250,  4.016250,  2.231250);  // 156
atom(.3,  1.338750,  3.123750,  1.338750);  // 157
atom(.3,  2.231250,  2.231250,  4.016250);  // 158
atom(.3,  1.338750,  1.338750,  3.123750);  // 159
//atom(.3,  4.016250,  4.016250,  4.016250);  // 160
atom(.3,  3.123750,  3.123750,  3.123750);  // 161
atom(.3,  4.016250,  2.231250,  5.798250);  // 162
atom(.3,  3.123750,  1.338750,  4.905750);  // 163
atom(.3,  2.231250,  4.016250,  5.798250);  // 164
atom(.3,  1.338750,  3.123750,  4.905750);  // 165
atom(.3,  2.231250,  2.231250,  7.583250);  // 166
atom(.3,  1.338750,  1.338750,  6.690750);  // 167
//atom(.3,  4.016250,  4.016250,  7.583250);  // 168
atom(.3,  3.123750,  3.123750,  6.690750);  // 169

atom(.3,  5.798250,  0.449250, -1.335750);  // 203
atom(.3,  4.905750, -0.443250, -2.228250);  // 204

atom(.3,  5.798250,  0.449250,  2.231250);  // 213
atom(.3,  4.905750, -0.443250,  1.338750);  // 214

atom(.3,  5.798250,  0.449250,  5.798250);  // 223
atom(.3,  4.905750, -0.443250,  4.905750);  // 224

atom(.3,  4.905750,  1.338750, -0.443250);  // 236

atom(.3,  4.905750,  1.338750,  3.123750);  // 244

atom(.3,  4.905750,  1.338750,  6.690750);  // 252
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

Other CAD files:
OpenSLS R1 hardware/Laser Cutting/facePlate.sldprt
OpenSLS R1 hardware/powder capture troughs and stand/short wall trough/d.sldprt
OpenSLS R1 hardware/powder capture troughs and stand/stand/q.sldprt
OpenSLS R2 hardware/Fabrication Files/Laser Cutting/2.83mm Acrylic/Powder Ducting/Receiving Surface.sldprt
Model Geometries/Reduced_diamond_lattice_in_box.stl
OpenSLS R1 hardware/Laser Cutting/TEST_PIECE.DXF
OpenSLS R1 hardware/Laser Cutting/TEST_PIECE.SLDDRW
OpenSLS R1 hardware/Laser Cutting/body r1.DXF
OpenSLS R1 hardware/Laser Cutting/body r1.SLDDRW
OpenSLS R1 hardware/Laser Cutting/bottomPlate.sldprt
OpenSLS R1 hardware/Laser Cutting/brace.SLDPRT
OpenSLS R1 hardware/Laser Cutting/gasket.sldprt
OpenSLS R1 hardware/Laser Cutting/gaskets.DXF
OpenSLS R1 hardware/Laser Cutting/gaskets.SLDDRW
OpenSLS R1 hardware/Laser Cutting/plate 1.DXF
OpenSLS R1 hardware/Laser Cutting/plate 1.SLDDRW
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

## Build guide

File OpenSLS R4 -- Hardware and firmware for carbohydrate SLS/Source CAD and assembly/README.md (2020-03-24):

There is not currently a complete assembly guide for the OpenSLS powder module. The easiest way to figure out how the parts fit together is to look at the CAD file and hide/show the different parts to see where they fit. To connect the acrylic pieces, use an M3 nut in the vertical slot, and an M3 screw (usually M3x12 or M3x14) to tighten the pieces together. M3 nuts and bolts are also used to secure the 3D printed pieces to the laser-cut acrylic body, and to connect the 3D printed pieces to each other. 

The powder spreader is a lab spatula (see BOM) which can attach to the servo motor via a 3D printed part. To connect the spatula to this connector, we use hot glue. We also use acrylic glue on all the tabbed inserts on the inside of the piston where powder could slip through. 

The CAD file was designed in Autodesk Fusion 360, which is free for educational use and by makers. A F360 archive file is included in the repo, or you can find it at: https://a360.co/2UAdHrG

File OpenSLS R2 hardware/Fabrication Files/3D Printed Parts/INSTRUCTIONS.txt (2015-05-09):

Print the following:

2x couple constraint.STL
2x distributor blade mount.STL
1x distributor motor mount A.STL
1x distributor motor mount B.STL
1x distributor r3-Belt block1.STL
1x distributor r3-Belt block2.STL
1x distributor r3-Blade frame.STL
3x distributor r3-CLamp block1.STL
1x distributor rail mount A.STL
1x distributor rail mount B.STL
1x feed piston acme plate.STL
4x integration bracket.STL
1x piston motor mount.STL
1x piston plate mount.STL
2x hopper lock clip

Detailed assembly instructions to come soon at andreasbastian.com/opensls

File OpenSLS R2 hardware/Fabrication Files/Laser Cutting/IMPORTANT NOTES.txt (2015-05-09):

Double check the layout for eahc DXF for overlaps/double cuts and for the appropriate line weight for vector cutting.

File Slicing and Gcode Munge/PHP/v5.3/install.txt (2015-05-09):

Installing PHP
     __________________________________________________________________

   Table of Contents
   Preface
   1. General Installation Considerations
   2. Installation on Windows systems

        Windows Installer
        Manual Installation Steps
        ActiveScript
        Microsoft IIS / PWS
        Apache 1.3.x on Microsoft Windows
        Apache 2.0.x on Microsoft Windows
        Sun, iPlanet and Netscape servers on Microsoft Windows
        OmniHTTPd Server
        Sambar Server on Microsoft Windows
        Xitami on Microsoft Windows
        Installation of extensions on Windows

   3. Installation of PECL extensions

        Introduction to PECL Installations
        Downloading PECL extensions
        PECL for Windows users
        Compiling shared PECL extensions with the pecl command
        Compiling shared PECL extensions with phpize
        Compiling PECL extensions statically into PHP

   4. Problems?

        Read the FAQ
        Other problems
        Bug reports

   5. Runtime Configuration

        The configuration file
        How to change configuration settings

   6. Installation FAQ
     __________________________________________________________________

Preface

   These installation instructions were generated from the HTML version of
   the PHP Manual so formatting and linking have been altered. See the
   online and updated version at: http://php.net/install.windows
     __________________________________________________________________

Chapter 1. General Installation Considerations

   Before starting the installation, first you need to know what do you
   want to use PHP for. There are three main fields you can use PHP, as
   described in the What can PHP do? section:

     * Websites and web applications (server-side scripting)
     * Command line scripting
     * Desktop (GUI) applications

   For the first and most common form, you need three things: PHP itself,
   a web server and a web browser. You probably already have a web
   browser, and depending on your operating system setup, you may also
   have a web server (e.g. Apache on Linux and MacOS X; IIS on Windows).
   You may also rent webspace at a company. This way, you don't need to
   set up anything on your own, only write your PHP scripts, upload it to
   the server you rent, and see the results in your browser.

   In case of setting up the server and PHP on your own, you have two
   choices for the method of connecting PHP to the server. For many
   servers PHP has a direct module interface (also called SAPI). These
   servers include Apache, Microsoft Internet Information Server, Netscape
   and iPlanet servers. Many other servers have support for ISAPI, the
   Microsoft module interface (OmniHTTPd for example). If PHP has no
   module support for your web server, you can always use it as a CGI or
   FastCGI processor. This means you set up your server to use the CGI
   executable of PHP to process all PHP file requests on the server.

   If you are also interested to use PHP for command line scripting (e.g.
   write scripts autogenerating some images for you offline, or processing
   text files depending on some arguments you pass to them), you always
   need the command line executable. For more information, read the
   section about writing command line PHP applications. In this case, you
   need no server and no browser.

   With PHP you can also write desktop GUI applications using the PHP-GTK
   extension. This is a completely different approach than writing web
   pages, as you do not output any HTML, but manage Windows and objects
   within them. For more information about PHP-GTK, please visit the site
   dedicated to this extension. PHP-GTK is not included in the official
   PHP distribution.

   From now on, this section deals with setting up PHP for web servers on
   Unix and Windows with server module interfaces and CGI executables. You
   will also find information on the command line executable in the
   following sections.

   PHP source code and binary distributions for Windows can be found at
   http://www.php.net/downloads.php. We recommend you to choose a mirror
   nearest to you for downloading the distributions.
     __________________________________________________________________

Chapter 2. Installation on Windows systems

   This section applies to Windows 98/Me and Windows NT/2000/XP/2003. PHP
   will not work on 16 bit platforms such as Windows 3.1 and sometimes we
   refer to the supported Windows platforms as Win32. Windows 95 is no
   longer supported as of PHP 4.3.0.

   There are two main ways to install PHP for Windows: either manually or
   by using the installer.

   If you have Microsoft Visual Studio, you can also build PHP from the
   original source code.

   Once you have PHP installed on your Windows system, you may also want
   to load various extensions for added functionality.

   Warning

   There are several all-in-one installers over the Internet, but none of
   those are endorsed by PHP.net, as we believe that the manual
   installation is the best choice to have your system secure and
   optimised.
     __________________________________________________________________

Windows Installer (PHP 5.2 and later)

   The Windows PHP installer for later versions of PHP is built using MSI
   technology using the Wix Toolkit (http://wix.sourceforge.net/). It will
   install and configure PHP and all the built-in and PECL extensions, as
   well as configure many of the popular web servers such as IIS, Apache,
   and Xitami.

   First, install your selected HTTP (web) server on your system, and make
   sure that it works. Then proceed with one of the following install
   types.
     __________________________________________________________________

Normal Install

   Run the MSI installer and follow the instructions provided by the
   installation wizard. You will be prompted to select the Web Server you
   wish to configure first, along with any configuration details needed.

   You will then be prompted to select which features and extensions you
   wish to install and enable. By selecting "Will be installed on local
   hard drive" in the drop-down menu for each item you can trigger whether
   to install the feature or not. By selecting "Entire feature will be
   installed on local hard drive", you will be able to install all
   sub-features of the included feature ( for example by selecting this
   options for the feature "PDO" you will install all PDO Drivers ).

   Warning

   It is not recommended to install all extensions by default, since many
   other them require dependencies from outside PHP in order to function
   properly. Instead, use the Installation Repair Mode that can be
   triggered thru the 'Add/Remove Programs' control panel to enable or
   disable extensions and features after installation.

   The installer then sets up PHP to be used in Windows and the php.ini
   file, and configures certain web servers to use PHP. The installer will
   currently configure IIS (CGI mode only), Apache, Xitami, and Sambar
   Server; if you are using a different web server you'll need to
   configure it manually.
     __________________________________________________________________

Silent Install

   The installer also supports a silent mode, which is helpful for Systems
   Administrators to deploy PHP easily. To use silent mode:
   msiexec.exe /i php-VERSION-win32-install.msi /q

   You can control the install directory by passing it as a parameter to
   the install. For example, to install to e:\php:
   msiexec.exe /i php-VERSION-win32-install.msi /q INSTALLDIR=e:\php

   You can also use the same syntax to specify the Apache Configuration
   Directory (APACHEDIR), the Sambar Server directory (SAMBARDIR), and the
   Xitami Server directory (XITAMIDIR).

   You can also specify what features to install. For example, to install
   the mysqli extension and the CGI executable:
   msiexec.exe /i php-VERSION-win32-install.msi /q ADDLOCAL=cgi,ext_php_mysqli

   The current list of Features to install is as follows:
MainExecutable - php.exe executable
ScriptExecutable - php-win.exe executable
ext_php_* - the various extensions ( for example: ext_php_mysql for MySQL )
apache13 - Apache 1.3 module
apache20 - Apache 2.0 module
apache22 - Apache 2,2 module
apacheCGI - Apache CGI executable
iis4ISAPI - IIS ISAPI module
iis4CGI - IIS CGI executable
NSAPI - Sun/iPlanet/Netscape server module
Xitami - Xitami CGI executable
Sambar - Sambar Server ISAPI module
CGI - php-cgi.exe executable
PEAR - PEAR installer
Manual - PHP Manual in CHM Format

   For more information on installing MSI installers from the command
   line, visit
   http://msdn.microsoft.com/library/en-us/msi/setup/command_line_options.
   asp
     __________________________________________________________________

Windows Installer (PHP 5.1.0 and earlier)

   The Windows PHP installer is available from the downloads page at
   http://www.php.net/downloads.php. This installs the CGI version of PHP
   and for IIS, PWS, and Xitami, it configures the web server as well. The
   installer does not include any extra external PHP extensions
   (php_*.dll) as you'll only find those in the Windows Zip Package and
   PECL downloads.

     Note: While the Windows installer is an easy way to make PHP work,
     it is restricted in many aspects as, for example, the automatic
     setup of extensions is not supported. Use of the installer isn't the
     preferred method for installing PHP.

   First, install your selected HTTP (web) server on your system, and make
   sure that it works.

   Run the executable installer and follow the instructions provided by
   the installation wizard. Two types of installation are supported -
   standard, which provides sensible defaults for all the settings it can,
   and advanced, which asks questions as it goes along.

   The installation wizard gathers enough information to set up the
   php.ini file, and configure certain web servers to use PHP. One of the
   web servers the PHP installer does not configure for is Apache, so
   you'll need to configure it manually.

   Once the installation has completed, the installer will inform you if
   you need to restart your system, restart the server, or just start
   using PHP.

   Warning

   Be aware, that this setup of PHP is not secure. If you would like to
   have a secure PHP setup, you'd better go on the manual way, and set
   every option carefully. This automatically working setup gives you an
   instantly working PHP installation, but it is not meant to be used on
   online servers.
     __________________________________________________________________

Manual Installation Steps

   This install guide will help you manually install and configure PHP
   with a web server on Microsoft Windows. To get started you'll need to
   download the zip binary distribution from the downloads page at
   http://www.php.net/downloads.php.

   Although there are many all-in-one installation kits, and we also
   distribute a PHP installer for Microsoft Windows, we recommend you take
   the time to setup PHP yourself as this will provide you with a better
   understanding of the system, and enables you to install PHP extensions
   easily when needed.

     Upgrading from a previous PHP version: Previous editions of the
     manual suggest moving various ini and DLL files into your SYSTEM
     (i.e. C:\WINDOWS) folder and while this simplifies the installation
     procedure it makes upgrading difficult. We advise you remove all of
     these files (like php.ini and PHP related DLLs from the Windows
     SYSTEM folder) before moving on with a new PHP installation. Be sure
     to backup these files as you might break the entire system. The old
     php.ini might be useful in setting up the new PHP as well. And as
     you'll soon learn, the preferred method for installing PHP is to
     keep all PHP related files in one directory and have this directory
     available to your systems PATH.

     MDAC requirements: If you use Microsoft Windows 98/NT4 download the
     latest version of the Microsoft Data Access Components (MDAC) for
     your platform. MDAC is available at http://msdn.microsoft.com/data/.
     This requirement exists because ODBC is built into the distributed
     Windows binaries.

   The following steps should be completed on all installations before any
   server specific instructions are performed:

   Extract the distribution file into a directory of your choice. If you
   are installing PHP 4, extract to C:\, as the zip file expands to a
   foldername like php-4.3.7-Win32. If you are installing PHP 5, extract
   to C:\php as the zip file doesn't expand as in PHP 4. You may choose a
   different location but do not have spaces in the path (like C:\Program
   Files\PHP) as some web servers will crash if you do.

   The directory structure extracted from the zip is different for PHP
   versions 4 and 5 and look like as follows:

   Example 2-2. PHP 5 package structure
c:\php
   |
   +--dev
   |  |
   |  |-php5ts.lib
   |
   +--ext                 -- extension DLLs for PHP
   |  |
   |  |-php_bz2.dll
   |  |
   |  |-php_cpdf.dll
   |  |
   |  |-..
   |
   +--extras
   |  |
   |  +--mibs             -- support files for SNMP
   |  |
   |  +--openssl          -- support files for Openssl
   |  |
   |  +--pdf-related      -- support files for PDF
   |  |
   |  |-mime.magic
   |
   +--pear                -- initial copy of PEAR
   |
   |
   |-go-pear.bat          -- PEAR setup script
   |
   |-fdftk.dll
   |
   |-..
   |
   |-php-cgi.exe          -- CGI executable
   |
   |-php-win.exe          -- executes scripts without an opened command prompt
   |
   |-php.exe              -- CLI executable - ONLY for command line scripting
   |
   |-..
   |
   |-php.ini-development  -- development php.ini settings
   |
   |-php.ini-production   -- recommended php.ini settings for production
   |
   |-php5activescript.dll
   |
   |-php5apache.dll
   |
   |-php5apache2.dll
   |
   |-..
   |
   |-php5ts.dll           -- core PHP DLL
   |
   |-...

   Notice the differences and similarities. Both PHP 4 and PHP 5 have a
   CGI executable, a CLI executable, and server modules, but they are
   located in different folders and/or have different names. While PHP 4
   packages have the server modules in the sapi folder, PHP 5
   distributions have no such directory and instead they're in the PHP
   folder root. The supporting DLLs for the PHP 5 extensions are also not
   in a seperate directory.

     Note: In PHP 4, you should move all files located in the dll and
     sapi folders to the main folder (e.g. C:\php).

   Here is a list of server modules shipped with PHP 5:

     * sapi/php5apache2_2.dll - Apache 2.2.x module.
     * sapi/php5apache.dll (php5apache.dll) - Apache 1.x module
     * sapi/php5apache2.dll (php5apache2.dll) -  - Apache 2.0.x module.
     * sapi/php5isapi.dll - ISAPI Module for ISAPI compliant web servers 
       like IIS 5.0 or newer. However the FCGI SAPI is recommended with 
       IIS
     * sapi/php5nsapi.dll (php5nsapi.dll) - Sun/iPlanet/Netscape server
       module.

   Server modules provide significantly better performance and additional
   functionality compared to the CGI binary. The FastCGI is significantly
   more stable and can be faster than the ISAPI module with IIS.
   The CLI version is designed to let you use PHP for command line 
   scripting. More information about CLI is available in the chapter 
   about using PHP from the command line.

   Warning

   The SAPI modules have been significantly improved as of the 4.1
   release, however, in older systems you may encounter server errors or
   other server modules failing, such as ASP.

   The CGI and CLI binaries, and the web server modules all require the
   php5ts.dll file to be available to them. You have to make
   sure that this file can be found by your PHP installation. The search
   order for this DLL is as follows:

     * The same directory from where php.exe is called, or in case you use
       a SAPI module, the web server's directory (e.g. C:\Program
       Files\Apache Group\Apache2\bin).
     * Any directory in your Windows PATH environment variable.

   To make php5ts.dll available you have three options: copy
   the file to the Windows system directory, copy the file to the web
   server's directory, or add your PHP directory, C:\php to the PATH. For
   better maintenance, we advise you to follow the last option, add C:\php
   to the PATH, because it will be simpler to upgrade PHP in the future.
   Read more about how to add your PHP directory to PATH in the
   corresponding FAQ entry (and then don't forget to restart the computer
   - logoff isn't enough).

   The next step is to set up a valid configuration file for PHP, php.ini.
   There are two ini files distributed in the zip file, php.ini-development
   and php.ini-production. We advise you to use php.ini-production, 
   because we optimized the default settings in this file for performance, 
   and security. Read this well documented file carefully because it has
   changes from php.ini-production that will drastically affect your setup.
   Some examples are display_errors being off and magic_quotes_gpc being off.
   In addition to reading these, study the ini settings and set every
   element manually yourself. If you would like to achieve the best
   security, then this is the way for you, although PHP works fine with
   these default ini files. Copy your chosen ini-file to a directory that
   PHP is able to find and rename it to php.ini. PHP searches for php.ini
   in the locations described in the Section called The configuration file
   in Chapter 5 section.

   If you are running Apache 2, the simpler option is to use the PHPIniDir
   directive (read the installation on Apache 2 page), otherwise your best
   option is to set the PHPRC environment variable. This process is
   explained in the following FAQ entry.

     Note: If you're using NTFS on Windows NT, 2000, XP or 2003, make
     sure that the user running the web server has read permissions to
     your php.ini (e.g. make it readable by Everyone).

   The following steps are optional:

     * Edit your new php.ini file. If you plan to use OmniHTTPd, do not
       follow the next step. Set the doc_root to point to your web servers
       document_root. For example:

doc_root = c:\inetpub\wwwroot // for IIS/PWS

doc_root = c:\apache\htdocs // for Apache

     * Choose the extensions you would like to load when PHP starts. See
       the section about Windows extensions, about how to set up one, and
       what is already built in. Note that on a new installation it is
       advisable to first get PHP working and tested without any
       extensions before enabling them in php.ini.
     * On PWS and IIS, you can set the browscap configuration setting to
       point to: c:\windows\system\inetsrv\browscap.ini on Windows 9x/Me,
       c:\winnt\system32\inetsrv\browscap.ini on NT/2000, and
       c:\windows\system32\inetsrv\browscap.ini on XP. For an up-to-date
       browscap.ini, read the following FAQ.

   PHP is now setup on your system. The next step is to choose a web
   server, and enable it to run PHP. Choose a web server from the table of
   contents.
     __________________________________________________________________

ActiveScript

   This section contains notes specific to the ActiveScript installation.

   ActiveScript is a Windows only SAPI that enables you to use PHP script
   in any ActiveScript compliant host, like Windows Script Host,
   ASP/ASP.NET, Windows Script Components or Microsoft Scriptlet control.

   As of PHP 5.0.1, ActiveScript has been moved to the PECL repository.
   The DLL for this PECL extension may be downloaded from either the PHP
   Downloads page or from http://pecl4win.php.net/

     Note: You should read the manual installation steps first!

   After installing PHP, you should download the ActiveScript DLL
   (php5activescript.dll) and place it in the main PHP folder (e.g.
   C:\php).

   After having all the files needed, you must register the DLL on your
   system. To achieve this, open a Command Prompt window (located in the
   Start Menu). Then go to your PHP directory by typing something like cd
   C:\php. To register the DLL just type regsvr32 php5activescript.dll.

   To test if ActiveScript is working, create a new file, named test.wsf
   (the extension is very important) and type:
<job id="test">

 <script language="PHPScript">
  $WScript->Echo("Hello World!");
 </script>

</job>

   Save and double-click on the file. If you receive a little window
   saying "Hello World!" you're done.

     Note: In PHP 4, the engine was named 'ActivePHP', so if you are
     using PHP 4, you should replace 'PHPScript' with 'ActivePHP' in the
     above example.

     Note: ActiveScript doesn't use the default php.ini file. Instead, it
     will look only in the same directory as the .exe that caused it to
     load. You should create php-activescript.ini and place it in that
     folder, if you wish to load extensions, etc.
     __________________________________________________________________

Microsoft IIS / PWS

   This section contains notes and hints specific to IIS (Microsoft
   Internet Information Server).

   Warning

   By using the CGI setup, your server is open to several possible
   attacks. Please read our CGI security section to learn how to defend
   yourself from those attacks.
     __________________________________________________________________

General considerations for all installations of PHP with IIS or PWS

     * First, read the Manual Installation Instructions. Do not skip this
       step as it provides crucial information for installing PHP on
       Windows.
     * CGI users must set the cgi.force_redirect PHP directive to 0 inside
       php.ini. Read the faq on cgi.force_redirect for important details.
       Also, CGI users may want to set the cgi.redirect_status_env
       directive. When using directives, be sure these directives aren't
       commented out inside php.ini.
     * The PHP 4 CGI is named php.exe while in PHP 5 it's php-cgi.exe. In
       PHP 5, php.exe is the CLI, and not the CGI.
     * Modify the Windows PATH environment variable to include the PHP
       directory. This way the PHP DLL files and PHP executables can all
       remain in the PHP directory without cluttering up the Windows
       system directory. For more details, see the FAQ on Setting the
       PATH.
     * The IIS user (usually IUSR_MACHINENAME) needs permission to read
       various files and directories, such as php.ini, docroot, and the
       session tmp directory.
     * Be sure the extension_dir and doc_root PHP directives are
       appropriately set in php.ini. These directives depend on the system
       that PHP is being installed on. In PHP 4, the extension_dir is
       extensions while with PHP 5 it's ext. So, an example PHP 5
       extensions_dir value is "c:\php\ext" and an example IIS doc_root
       value is "c:\Inetpub\wwwroot".
     * PHP extension DLL files, such as php_mysql.dll and php_curl.dll,
       are found in the zip package of the PHP download (not the PHP
       installer). In PHP 5, many extensions are part of PECL and can be
       downloaded in the "Collection of PECL modules" package. Files such
       as php_zip.dll and php_ssh2.dll. Download PHP files here.
     * When defining the executable, the 'check that file exists' box may
       also be checked. For a small performance penalty, the IIS (or PWS)
       will check that the script file exists and sort out authentication
       before firing up PHP. This means that the web server will provide
       sensible 404 style error messages instead of CGI errors complaining
       that PHP did not output any data.
     __________________________________________________________________

Windows NT/200x/XP and IIS 4 or newer

   PHP may be installed as a CGI binary, or with the ISAPI module. In
   either case, you need to start the Microsoft Management Console (may
   appear as 'Internet Services Manager', either in your Windows NT 4.0
   Option Pack branch or the Control Panel=>Administrative Tools under
   Windows 2000/XP). Then right click on your Web server node (this will
   most probably appear as 'Default Web Server'), and select 'Properties'.

   If you want to use the CGI binary, do the following:

     * Under 'Home Directory', 'Virtual Directory', or 'Directory', do the
       following:
     * Change the Execute Permissions to 'Scripts only'
     * Click on the 'Configuration' button, and choose the Application
       Mappings tab. Click Add and set the Executable path to the
       appropriate CGI file. An example PHP 5 value is: C:\php\php-cgi.exe
       Supply .php as the extension. Leave 'Method exclusions' blank, and
       check the 'Script engine' checkbox. Now, click OK a few times.
     * Set up the appropriate security. (This is done in Internet Service
       Manager), and if your NT Server uses NTFS file system, add execute
       rights for I_USR_ to the directory that contains php.exe /
       php-cgi.exe.

   To use the ISAPI module, do the following:

     * If you don't want to perform HTTP Authentication using PHP, you can
       (and should) skip this step. Under ISAPI Filters, add a new ISAPI
       filter. Use PHP as the filter name, and supply a path to the
       php5isapi.dll.
     * Under 'Home Directory', 'Virtual Directory', or 'Directory', do the
       following:
     * Change the Execute Permissions to 'Scripts only'
     * Click on the 'Configuration' button, and choose the Application
       Mappings tab. Click Add and set the Executable path to the
       appropriate ISAPI DLL. An example PHP 5 value is:
       C:\php\php5isapi.dll Supply .php as the extension. Leave 'Method
       exclusions' blank, and check the 'Script engine' checkbox. Now,
       click OK a few times.
     * Stop IIS completely (NET STOP iisadmin)
     * Start IIS again (NET START w3svc)

   With IIS 6 (2003 Server), open up the IIS Manager, go to Web Service
   Extensions, choose "Add a new Web service extension", enter in a name
   such as PHP, choose the Add button and for the value browse to either
   the ISAPI file (php5isapi.dll) or CGI (php.exe or
   php-cgi.exe) then check "Set extension status to Allowed" and click OK.

   In order to use index.php as a default content page, do the following:
   From within the Documents tab, choose Add. Type in index.php and click
   OK. Adjust the order by choosing Move Up or Move Down. This is similar
   to setting DirectoryIndex with Apache.

   The steps above must be repeated for each extension that is to be
   associated with PHP scripts. .php is the most common although .php3 may
   be required for legacy applications.

   If you experience 100% CPU usage after some time, turn off the IIS
   setting Cache ISAPI Application.
     __________________________________________________________________

Windows and IIS

See http://www.php.net/install.windows
     __________________________________________________________________

Apache 1.3.x on Microsoft Windows

   This section contains notes and hints specific to Apache 1.3.x installs
   of PHP on Microsoft Windows systems. There are also instructions and
   notes for Apache 2 on a separate page.

     Note: Please read the manual installation steps first!

   There are two ways to set up PHP to work with Apache 1.3.x on Windows.
   One is to use the CGI binary (php.exe for PHP 4 and php-cgi.exe for PHP
   5), the other is to use the Apache Module DLL. In either case you need
   to edit your httpd.conf to configure Apache to work with PHP, and then
   restart the server.

   It is worth noting here that now the SAPI module has been made more
   stable under Windows, we recommend it's use above the CGI binary, since
   it is more transparent and secure.

   Although there can be a few variations of configuring PHP under Apache,
   these are simple enough to be used by the newcomer. Please consult the
   Apache Documentation for further configuration directives.

   After changing the configuration file, remember to restart the server,
   for example, NET STOP APACHE followed by NET START APACHE, if you run
   Apache as a Windows Service, or use your regular shortcuts.

     Note: Remember that when adding path values in the Apache
     configuration files on Windows, all backslashes such as
     c:\directory\file.ext must be converted to forward slashes, as
     c:/directory/file.ext. A trailing slash may also be necessary for
     directories.
     __________________________________________________________________

Installing as an Apache module

   You should add the following lines to your Apache httpd.conf file:

   Example 2-3. PHP as an Apache 1.3.x module

   This assumes PHP is installed to c:\php. Adjust the path if this is not
   the case.

   For PHP 5:
# Add to the end of the LoadModule section
LoadModule php5_module "C:/php/php5apache.dll"

# Add to the end of the AddModule section
AddModule mod_php5.c

   For both:
# Add this line inside the <IfModule mod_mime.c> conditional brace
AddType application/x-httpd-php .php

# For syntax highlighted .phps files, also add
AddType application/x-httpd-php-source .phps
     __________________________________________________________________

Installing as a CGI binary

   If you unzipped the PHP package to C:\php\ as described in the Manual
   Installation Steps section, you need to insert these lines to your
   Apache configuration file to set up the CGI binary:

   Example 2-4. PHP and Apache 1.3.x as CGI
ScriptAlias /php/ "c:/php/"
AddType application/x-httpd-php .php

# For PHP 4
Action application/x-httpd-php "/php/php.exe"

# For PHP 5
Action application/x-httpd-php "/php/php-cgi.exe"

# specify the directory where php.ini is
SetEnv PHPRC C:/php

   Note that the second line in the list above can be found in the actual
   versions of httpd.conf, but it is commented out. Remember also to
   substitute the c:/php/ for your actual path to PHP.

   Warning

   By using the CGI setup, your server is open to several possible
   attacks. Please read our CGI security section to learn how to defend
   yourself from those attacks.

   If you would like to present PHP source files syntax highlighted, there
   is no such convenient option as with the module version of PHP. If you
   chose to configure Apache to use PHP as a CGI binary, you will need to
   use the highlight_file() function. To do this simply create a PHP
   script file and add this code: <?php
   highlight_file('some_php_script.php'); ?>.
     __________________________________________________________________

Apache 2.0.x on Microsoft Windows

   This section contains notes and hints specific to Apache 2.0.x installs
   of PHP on Microsoft Windows systems. We also have instructions and
   notes for Apache 1.3.x users on a separate page.

     Note: You should read the manual installation steps first!

     Apache 2.2.x Support: Users of Apache 2.2.x may use the
     documentation below except the appropriate DLL file is named
     php5apache2_2.dll and it only exists as of PHP 5.2.0. See also
     http://snaps.php.net/

   Warning

   We do not recommend using a threaded MPM in production with Apache2.
   Use the prefork MPM instead, or use Apache1. For information on why,
   read the related FAQ entry on using Apache2 with a threaded MPM

   You are highly encouraged to take a look at the Apache Documentation to
   get a basic understanding of the Apache 2.0.x Server. Also consider to
   read the Windows specific notes for Apache 2.0.x before reading on
   here.

     PHP and Apache 2.0.x compatibility notes: The following versions of
     PHP are known to work with the most recent version of Apache 2.0.x:

     * PHP 4.3.0 or later available at http://www.php.net/downloads.php.
     * the latest stable development version. Get the source code
       http://snaps.php.net/php5-latest.tar.gz or download binaries for
       Windows http://snaps.php.net/win32/php5-win32-latest.zip.
     * a prerelease version downloadable from http://qa.php.net/.
     * you have always the option to obtain PHP through SVN.

     These versions of PHP are compatible to Apache 2.0.40 and later.

     Apache 2.0 SAPI-support started with PHP 4.2.0. PHP 4.2.3 works with
     Apache 2.0.39, don't use any other version of Apache with PHP 4.2.3.
     However, the recommended setup is to use PHP 4.3.0 or later with the
     most recent version of Apache2.

     All mentioned versions of PHP will work still with Apache 1.3.x.

   Warning

   Apache 2.0.x is designed to run on Windows NT 4.0, Windows 2000 or
   Windows XP. At this time, support for Windows 9x is incomplete. Apache
   2.0.x is not expected to work on those platforms at this time.

   Download the most recent version of Apache 2.0.x and a fitting PHP
   version. Follow the Manual Installation Steps and come back to go on
   with the integration of PHP and Apache.

   There are two ways to set up PHP to work with Apache 2.0.x on Windows.
   One is to use the CGI binary the other is to use the Apache module DLL.
   In either case you need to edit your httpd.conf to configure Apache to
   work with PHP and then restart the server.

     Note: Remember that when adding path values in the Apache
     configuration files on Windows, all backslashes such as
     c:\directory\file.ext must be converted to forward slashes, as
     c:/directory/file.ext. A trailing slash may also be necessary for
     directories.
     __________________________________________________________________

Installing as a CGI binary

   You need to insert these three lines to your Apache httpd.conf
   configuration file to set up the CGI binary:

   Example 2-5. PHP and Apache 2.0 as CGI
ScriptAlias /php/ "c:/php/"
AddType application/x-httpd-php .php

# For PHP 4
Action application/x-httpd-php "/php/php.exe"

# For PHP 5
Action application/x-httpd-php "/php/php-cgi.exe"

   Warning

   By using the CGI setup, your server is open to several possible
   attacks. Please read our CGI security section to learn how to defend
   yourself from those attacks.
     __________________________________________________________________

Installing as an Apache module

   You need to insert these two lines to your Apache httpd.conf
   configuration file to set up the PHP module for Apache 2.0:

   Example 2-6. PHP and Apache 2.0 as Module

# For PHP 5 do something like this:
LoadModule php5_module "c:/php/php5apache2.dll"
AddType application/x-httpd-php .php

# configure the path to php.ini
PHPIniDir "C:/php"

     Note: Remember to substitute your actual path to PHP for the c:/php/
     in the above examples. Take care to use either 
     php5apache2.dll in your LoadModule directive and not php5apache.dll 
     as the latter ones are designed to run with Apache 1.3.x.

     Note: If you want to use content negotiation, read related FAQ.

   Warning

   Don't mix up your installation with DLL files from different PHP
   versions. You have the only choice to use the DLL's and extensions that
   ship with your downloaded PHP version.
     __________________________________________________________________

Sun, iPlanet and Netscape servers on Microsoft Windows

   This section contains notes and hints specific to Sun Java System Web
   Server, Sun ONE Web Server, iPlanet and Netscape server installs of PHP
   on Windows.

   From PHP 4.3.3 on you can use PHP scripts with the NSAPI module to
   generate custom directory listings and error pages. Additional
   functions for Apache compatibility are also available. For support in
   current web servers read the note about subrequests.
     __________________________________________________________________

CGI setup on Sun, iPlanet and Netscape servers

   To install PHP as a CGI handler, do the following:

     * Copy php5ts.dll to your systemroot (the directory where you
       installed Windows)
     * Make a file association from the command line. Type the following
       two lines:

assoc .php=PHPScript
ftype PHPScript=c:\php\php.exe %1 %*

     * In the Netscape Enterprise Administration Server create a dummy
       shellcgi directory and remove it just after (this step creates 5
       important lines in obj.conf and allow the web server to handle
       shellcgi scripts).
     * In the Netscape Enterprise Administration Server create a new mime
       type (Category: type, Content-Type: magnus-internal/shellcgi, File
       Suffix:php).
     * Do it for each web server instance you want PHP to run

   More details about setting up PHP as a CGI executable can be found
   here: http://benoit.noss.free.fr/php/install-php.html
     __________________________________________________________________

NSAPI setup on Sun, iPlanet and Netscape servers

   To install PHP with NSAPI, do the following:

     * Copy php5ts.dll to your systemroot (the directory where you
       installed Windows)
     * Make a file association from the command line. Type the following
       two lines:

assoc .php=PHPScript
ftype PHPScript=c:\php\php.exe %1 %*

     * In the Netscape Enterprise Administration Server create a new mime
       type (Category: type, Content-Type: magnus-internal/x-httpd-php,
       File Suffix: php).
     * Edit magnus.conf (for servers >= 6) or obj.conf (for servers < 6)
       and add the following: You should place the lines after mime types
       init.

Init fn="load-modules" funcs="php5_init,php5_execute,php5_auth_trans" shlib="c:/
php/sapi/php5nsapi.dll"
Init fn="php5_init" LateInit="yes" errorString="Failed to initialise PHP!" [php_
ini="c:/path/to/php.ini"]

       The php_ini parameter is optional but with it you
       can place your php.ini in your web server configuration directory.
     * Configure the default object in obj.conf (for virtual server
       classes [Sun Web Server 6.0+] in their vserver.obj.conf): In the
       <Object name="default"> section, place this line necessarily after
       all 'ObjectType' and before all 'AddLog' lines:

Service fn="php5_execute" type="magnus-internal/x-httpd-php" [inikey=value inike
y=value ...]

       As additional parameters you can add some special
       php.ini-values, for example you can set a
       docroot="/path/to/docroot" specific to the context php5_execute is
       called. For boolean ini-keys please use 0/1 as value, not
       "On","Off",... (this will not work correctly), e.g.
       zlib.output_compression=1 instead of zlib.output_compression="On"
     * This is only needed if you want to configure a directory that only
       consists of PHP scripts (same like a cgi-bin directory):

<Object name="x-httpd-php">
ObjectType fn="force-type" type="magnus-internal/x-httpd-php"
Service fn=php5_execute [inikey=value inikey=value ...]
</Object>

       After that you can configure a directory in the Administration
       server and assign it the style x-httpd-php. All files in it will
       get executed as PHP. This is nice to hide PHP usage by renaming
       files to .html.
     * Restart your web service and apply changes
     * Do it for each web server instance you want PHP to run

     Note: More details about setting up PHP as an NSAPI filter can be
     found here: http://benoit.noss.free.fr/php/install-php4.html

     Note: The stacksize that PHP uses depends on the configuration of
     the web server. If you get crashes with very large PHP scripts, it
     is recommended to raise it with the Admin Server (in the section
     "MAGNUS EDITOR").
     __________________________________________________________________

CGI environment and recommended modifications in php.ini

   Important when writing PHP scripts is the fact that Sun JSWS/Sun ONE
   WS/iPlanet/Netscape is a multithreaded web server. Because of that all
   requests are running in the same process space (the space of the web
   server itself) and this space has only one environment. If you want to
   get CGI variables like PATH_INFO, HTTP_HOST etc. it is not the correct
   way to try this in the old PHP 3.x way with getenv() or a similar way
   (register globals to environment, $_ENV). You would only get the
   environment of the running web server without any valid CGI variables!

     Note: Why are there (invalid) CGI variables in the environment?

     Answer: This is because you started the web server process from the
     admin server which runs the startup script of the web server, you
     wanted to start, as a CGI script (a CGI script inside of the admin
     server!). This is why the environment of the started web server has
     some CGI environment variables in it. You can test this by starting
     the web server not from the administration server. Use the command
     line as root user and start it manually - you will see there are no
     CGI-like environment variables.

   Simply change your scripts to get CGI variables in the correct way for
   PHP 5.x by using the superglobal $_SERVER. If you have older scripts
   which use $HTTP_HOST, etc., you should turn on register_globals in
   php.ini and change the variable order too (important: remove "E" from
   it, because you do not need the environment here):
variables_order = "GPCS"
register_globals = On
     __________________________________________________________________

Special use for error pages or self-made directory listings (PHP >= 4.3.3)

   You can use PHP to generate the error pages for "404 Not Found" or
   similar. Add the following line to the object in obj.conf for every
   error page you want to overwrite:
Error fn="php5_execute" code=XXX script="/path/to/script.php" [inikey=value inik
ey=value...]

   where XXX is the HTTP error code. Please delete any other Error
   directives which could interfere with yours. If you want to place a
   page for all errors that could exist, leave the code parameter out.
   Your script can get the HTTP status code with $_SERVER['ERROR_TYPE'].

   Another possibility is to generate self-made directory listings. Just
   create a PHP script which displays a directory listing and replace the
   corresponding default Service line for type="magnus-internal/directory"
   in obj.conf with the following:
Service fn="php5_execute" type="magnus-internal/directory" script="/path/to/scri
pt.php" [inikey=value inikey=value...]

   For both error and directory listing pages the original URI and
   translated URI are in the variables $_SERVER['PATH_INFO'] and
   $_SERVER['PATH_TRANSLATED'].
     __________________________________________________________________

Note about nsapi_virtual() and subrequests (PHP >= 4.3.3)

   The NSAPI module now supports the nsapi_virtual() function (alias:
   virtual()) to make subrequests on the web server and insert the result
   in the web page. The problem is, that this function uses some
   undocumented features from the NSAPI library.

   Under Unix this is not a problem, because the module automatically
   looks for the needed functions and uses them if available. If not,
   nsapi_virtual() is disabled.

   Under Windows limitations in the DLL handling need the use of a
   automatic detection of the most recent ns-httpdXX.dll file. This is
   tested for servers till version 6.1. If a newer version of the Sun
   server is used, the detection fails and nsapi_virtual() is disabled.

   If this is the case, try the following: Add the following parameter to
   php5_init in magnus.conf/obj.conf:
   Init fn=php5_init ... server_lib="ns-httpdXX.dll"

   where XX is the correct DLL version number. To get it, look in the
   server-root for the correct DLL name. The DLL with the biggest filesize
   is the right one.

   You can check the status by using the phpinfo() function.

     Note: But be warned: Support for nsapi_virtual() is EXPERIMENTAL!!!
     __________________________________________________________________

OmniHTTPd Server

   This section contains notes and hints specific to OmniHTTPd on Windows.

     Note: You should read the manual installation steps first!

   Warning

   By using the CGI setup, your server is open to several possible
   attacks. Please read our CGI security section to learn how to defend
   yourself from those attacks.

   You need to complete the following steps to make PHP work with
   OmniHTTPd. This is a CGI executable setup. SAPI is supported by
   OmniHTTPd, but some tests have shown that it is not so stable to use
   PHP as an ISAPI module.

     Important for CGI users: Read the faq on cgi.force_redirect for
     important details. This directive needs to be set to 0.

    1. Install OmniHTTPd server.
    2. Right click on the blue OmniHTTPd icon in the system tray and
       select Properties
    3. Click on Web Server Global Settings
    4. On the 'External' tab, enter: virtual = .php | actual =
       c:\php\php.exe (use php-cgi.exe if installing PHP 5), and use the
       Add button.
    5. On the Mime tab, enter: virtual = wwwserver/stdcgi | actual = .php,
       and use the Add button.
    6. Click OK

   Repeat steps 2 - 6 for each extension you want to associate with PHP.

     __________________________________________________________________

Xitami on Microsoft Windows

   This section contains notes and hints specific to Xitami on Windows.

     Note: You should read the manual installation steps first!

   This list describes how to set up the PHP CGI binary to work with
   Xitami on Windows.

     Important for CGI users: Read the faq on cgi.force_redirect for
     important details. This directive needs to be set to 0. If you want
     to use $_SERVER['PHP_SELF'] you have to enable the cgi.fix_pathinfo
     directive.

   Warning

   By using the CGI setup, your server is open to several possible
   attacks. Please read our CGI security section to learn how to defend
   yourself from those attacks.

     * Make sure the web server is running, and point your browser to
       xitamis admin console (usually http://127.0.0.1/admin), and click
       on Configuration.
     * Navigate to the Filters, and put the extension which PHP should
       parse (i.e. .php) into the field File extensions (.xxx).
     * In Filter command or script put the path and name of your PHP CGI
       executable i.e. C:\php\php-cgi.exe.
     * Press the 'Save' icon.
     * Restart the server to reflect changes.
     __________________________________________________________________

Installation of extensions on Windows

   After installing PHP and a web server on Windows, you will probably
   want to install some extensions for added functionality. You can choose
   which extensions you would like to load when PHP starts by modifying
   your php.ini. You can also load a module dynamically in your script
   using dl().

   The DLLs for PHP extensions are prefixed with php_.

   Many extensions are built into the Windows version of PHP. This means
   additional DLL files, and the extension directive, are not used to load
   these extensions. The Windows PHP Extensions table lists extensions
   that require, or used to require, additional PHP DLL files. Here's a
   list of built in extensions:

   In PHP 5 (updated PHP 5.0.4), the following changes exist. Built in:
   DOM, LibXML, Iconv, SimpleXML, SPL and SQLite. And the following are no
   longer built in: MySQL and Overload.

   The default location PHP searches for extensions is C:\php5 in PHP 5. 
   To change this setting to reflect your setup of PHP edit your php.ini
   file:

     * You will need to change the extension_dir setting to point to the
       directory where your extensions lives, or where you have placed
       your php_*.dll files. For example:

extension_dir = C:\php\extensions

     * Enable the extension(s) in php.ini you want to use by uncommenting
       the extension=php_*.dll lines in php.ini. This is done by deleting
       the leading ; from the extension you want to load.

   Example 2-8. Enable Bzip2 extension for PHP-Windows
// change the following line from ...
;extension=php_bz2.dll

// ... to
extension=php_bz2.dll

     * Some of the extensions need extra DLLs to work. Couple of them can
       be found in the distribution package, in in the main folder in PHP 5, 
       but some, for example Oracle (php_oci8.dll) require DLLs which are 
       not bundled with the distribution package.
     * Some of these DLLs are not bundled with the PHP distribution. See
       each extensions documentation page for details. Also, read the
       manual section titled Installation of PECL extensions for details
       on PECL. An increasingly large number of PHP extensions are found
       in PECL, and these extensions require a separate download.

     Note: If you are running a server module version of PHP remember to
     restart your web server to reflect your changes to php.ini.

   The following table describes some of the extensions available and
   required additional dlls.

   Table 2-1. PHP Extensions
   Extension Description Notes
   php_bz2.dll bzip2 compression functions None
   php_calendar.dll Calendar conversion functions
   php_cpdf.dll ClibPDF functions None
   php_crack.dll Crack functions None
   php_ctype.dll ctype family functions
   php_curl.dll CURL, Client URL library functions Requires: libeay32.dll,
   ssleay32.dll (bundled)
   php_db.dll DBM functions Deprecated. Use DBA instead (php_dba.dll)
   php_dba.dll DBA: DataBase (dbm-style) Abstraction layer functions None
   php_dbase.dll dBase functions None
   php_dbx.dll dbx functions
   php_exif.dll EXIF functions php_mbstring.dll. And, php_exif.dll must be
   loaded after php_mbstring.dll in php.ini.
   php_fdf.dll FDF: Forms Data Format functions. Requires: fdftk.dll
   (bundled)
   php_filepro.dll filePro functions Read-only access
   php_ftp.dll FTP functions
   php_gd2.dll GD library image functions GD2
   php_gettext.dll Gettext functions, requires libintl-1.dll, 
   iconv.dll (bundled).
   php_iconv.dll ICONV characterset conversion Requires: iconv.dll
   php_imap.dll IMAP POP3 and NNTP functions None
   php_interbase.dll InterBase functions Requires: gds32.dll (bundled)
   php_ldap.dll LDAP functions requires libeay32.dll, ssleay32.dll (bundled)
   php_mbstring.dll Multi-Byte String functions None
   php_mcrypt.dll Mcrypt Encryption functions Requires: libmcrypt.dll
   php_mime_magic.dll Mimetype functions Requires: magic.mime (bundled)
   php_ming.dll Ming functions for Flash None
   php_msql.dll mSQL functions Requires: msql.dll (bundled)
   php_mssql.dll MSSQL functions Requires: ntwdblib.dll (bundled)
   php_mysql.dll MySQL functions PHP >= 5.0.0, requires libmysql.dll
   (bundled)
   php_mysqli.dll MySQLi functions PHP >= 5.0.0, requires libmysql.dll
   (libmysqli.dll in PHP <= 5.0.2) (bundled)
   php_oci8.dll Oracle 8 functions Requires: Oracle 8.1+ client libraries
   php_openssl.dll OpenSSL functions Requires: libeay32.dll (bundled)
   php_oracle.dll Oracle functions Requires: Oracle 7 client libraries
   php_pgsql.dll PostgreSQL functions None
   php_printer.dll Printer functions None
   php_shmop.dll Shared Memory functions None
   php_snmp.dll SNMP get and walk functions NT only!
   php_soap.dll SOAP functions PHP >= 5.0.0
   php_sockets.dll Socket functions None
   php_sybase_ct.dll Sybase functions Requires: Sybase client libraries
   php_tidy.dll Tidy functions PHP >= 5.0.0
   php_tokenizer.dll Tokenizer functions Built in since PHP 4.3.0
   php_xmlrpc.dll XML-RPC functions PHP >= 4.2.1 requires: iconv.dll
   (bundled)
   php_xslt.dll XSLT requires libxslt.dll, iconv.dll (bundled).
   php_zip.dll Zip File functions
   php_zlib.dll ZLib compression functions
     __________________________________________________________________

Chapter 3. Installation of PECL extensions

Introduction to PECL Installations

   PECL is a repository of PHP extensions that are made available to you
   via the PEAR packaging system. This section of the manual is intended
   to demonstrate how to obtain and install PECL extensions.

   These instructions assume /your/phpsrcdir/ is the path to the PHP
   source distribution, and that extname is the name of the PECL
   extension. Adjust accordingly. These instructions also assume a
   familiarity with the pear command. The information in the PEAR manual
   for the pear command also applies to the pecl command.

   To be useful, a shared extension must be built, installed, and loaded.
   The methods described below provide you with various instructions on
   how to build and install the extensions, but they do not automatically
   load them. Extensions can be loaded by adding an extension directive.
   To this php.ini file, or through the use of the dl() function.

   When building PHP modules, it's important to have known-good versions
   of the required tools (autoconf, automake, libtool, etc.) See the
   SVN Instructions for details on the required tools, and required 
   versions.
     __________________________________________________________________

Downloading PECL extensions

   There are several options for downloading PECL extensions, such as:

     * http://pecl.php.net
       The PECL web site contains information about the different
       extensions that are offered by the PHP Development Team. The
       information available here includes: ChangeLog, release notes,
       requirements and other similar details.
     * pecl download extname
       PECL extensions that have releases listed on the PECL web site are
       available for download and installation using the pecl command.
       Specific revisions may also be specified.
     * SVN 
       Most PECL extensions also reside in SVN. A web-based view may be
       seen at http://svn.php.net/pecl/. To download straight from SVN,
       the following sequence of commands may be used. 

$ svn  co http://svn.php.net/repository/pecl/<extname>/trunk

     * Windows downloads
       Windows users may find compiled PECL binaries by downloading the
       Collection of PECL modules from the PHP Downloads page, or by
       retrieving a PECL Snapshot or an extension DLL on PECL4WIN. To
       compile PHP under Windows, read the appropriate chapter.
     __________________________________________________________________

PECL for Windows users

   As with any other PHP extension DLL, installation is as simple as
   copying the PECL extension DLLs into the extension_dir folder and
   loading them from php.ini. For example, add the following line to your
   php.ini:

   extension=php_extname.dll

   After doing this, restart the web server.
     __________________________________________________________________

Compiling shared PECL extensions with the pecl command

   PECL makes it easy to create shared PHP extensions. Using the pecl
   command, do the following:

   $ pecl install extname

   This will download the source for extname, compile, and install
   extname.so into your extension_dir. extname.so may then be loaded via
   php.ini

   By default, the pecl command will not install packages that are marked
   with the alpha or beta state. If no stable packages are available, you
   may install a beta package using the following command:

   $ pecl install extname-beta

   You may also install a specific version using this variant:

   $ pecl install extname-0.1
     __________________________________________________________________

Compiling shared PECL extensions with phpize

   Sometimes, using the pecl installer is not an option. This could be
   because you're behind a firewall, or it could be because the extension
   you want to install is not available as a PECL compatible package, such
   as unreleased extensions from SVN. If you need to build such an
   extension, you can use the lower-level build tools to perform the build
   manually.

   The phpize command is used to prepare the build environment for a PHP
   extension. In the following sample, the sources for an extension are in
   a directory named extname:

$ cd extname
$ phpize
$ ./configure
$ make
# make install

   A successful install will have created extname.so and put it into the
   PHP extensions directory. You'll need to and adjust php.ini and add an
   extension=extname.so line before you can use the extension.

   If the system is missing the phpize command, and precompiled packages
   (like RPM's) are used, be sure to also install the appropriate devel
   version of the PHP package as they often include the phpize command
   along with the appropriate header files to build PHP and its
   extensions.

   Execute phpize --help to display additional usage information.
     __________________________________________________________________

Compiling PECL extensions statically into PHP

   You might find that you need to build a PECL extension statically into
   your PHP binary. To do this, you'll need to place the extension source
   under the php-src/ext/ directory and tell the PHP build system to
   regenerate its configure script.

$ cd /your/phpsrcdir/ext
$ pecl download extname
$ gzip -d < extname.tgz | tar -xvf -
$ mv extname-x.x.x extname

   This will result in the following directory:

   /your/phpsrcdir/ext/extname

   From here, force PHP to rebuild the configure script, and then build
   PHP as normal:

$ cd /your/phpsrcdir
$ rm configure
$ ./buildconf --force
$ ./configure --help
$ ./configure --with-extname --enable-someotherext --with-foobar
$ make
$ make install

     Note: To run the 'buildconf' script you need autoconf 2.13 and
     automake 1.4+ (newer versions of autoconf may work, but are not
     supported).

   Whether --enable-extname or --with-extname is used depends on the
   extension. Typically an extension that does not require external
   libraries uses --enable. To be sure, run the following after buildconf:

   $ ./configure --help | grep extname
     __________________________________________________________________

Chapter 4. Problems?

Read the FAQ

   Some problems are more common than others. The most common ones are
   listed in the PHP FAQ, part of this manual.
     __________________________________________________________________

Other problems

   If you are still stuck, someone on the PHP installation mailing list
   may be able to help you. You should check out the archive first, in
   case someone already answered someone else who had the same problem as
   you. The archives are available from the support page on
   http://www.php.net/support.php. To subscribe to the PHP installation
   mailing list, send an empty mail to
   php-install-subscribe@lists.php.net. The mailing list address is
   php-install@lists.php.net.

   If you want to get help on the mailing list, please try to be precise
   and give the necessary details about your environment (which operating
   system, what PHP version, what web server, if you are running PHP as
   CGI or a server module, safe mode, etc...), and preferably enough code
   to make others able to reproduce and test your problem.
     __________________________________________________________________

Bug reports

   If you think you have found a bug in PHP, please report it. The PHP
   developers probably don't know about it, and unless you report it,
   chances are it won't be fixed. You can report bugs using the
   bug-tracking system at http://bugs.php.net/. Please do not send bug
   reports in mailing list or personal letters. The bug system is also
   suitable to submit feature requests.

   Read the How to report a bug document before submitting any bug
   reports!
     __________________________________________________________________

Chapter 5. Runtime Configuration

The configuration file

   The configuration file (called php3.ini in PHP 3, and simply php.ini as
   of PHP 4) is read when PHP starts up. For the server module versions of
   PHP, this happens only once when the web server is started. For the CGI
   and CLI version, it happens on every invocation.

   php.ini is searched in these locations (in order):

     * SAPI module specific location (PHPIniDir directive in Apache 2, -c
       command line option in CGI and CLI, php_ini parameter in NSAPI,
       PHP_INI_PATH environment variable in THTTPD)
     * The PHPRC environment variable. Before PHP 5.2.0 this was checked
       after the registry key mentioned below.
     * As of PHP 5.2.0, the following registry locations are searched in
       order: HKEY_LOCAL_MACHINE\SOFTWARE\PHP\x.y.z\IniFilePath,
       HKEY_LOCAL_MACHINE\SOFTWARE\PHP\x.y\IniFilePath and
       HKEY_LOCAL_MACHINE\SOFTWARE\PHP\x\IniFilePath, where x, y and z
       mean the PHP major, minor and release versions.
     * HKEY_LOCAL_MACHINE\SOFTWARE\PHP\IniFilePath (Windows Registry
       location)
     * Current working directory (except CLI)
     * The web server's directory (for SAPI modules), or directory of PHP
       (otherwise in Windows)
     * Windows directory (C:\windows or C:\winnt) (for Windows), or
       --with-config-file-path compile time option

   If php-SAPI.ini exists (where SAPI is used SAPI, so the filename is
   e.g. php-cli.ini or php-apache.ini), it's used instead of php.ini. SAPI
   name can be determined by php_sapi_name().

     Note: The Apache web server changes the directory to root at startup
     causing PHP to attempt to read php.ini from the root filesystem if
     it exists.

   The php.ini directives handled by extensions are documented
   respectively on the pages of the extensions themselves. The list of the
   core directives is available in the appendix. Probably not all PHP
   directives are documented in the manual though. For a complete list of
   directives available in your PHP version, please read your well
   commented php.ini file. Alternatively, you may find the latest
   php.ini from SVN helpful too.

   Example 5-1. php.ini example
; any text on a line after an unquoted semicolon (;) is ignored
[php] ; section markers (text within square brackets) are also ignored
; Boolean values can be set to either:
;    true, on, yes
; or false, off, no, none
register_globals = off
track_errors = yes

; you can enclose strings in double-quotes
include_path = ".:/usr/local/lib/php"

; backslashes are treated the same as any other character
include_path = ".;c:\php\lib"

   Since PHP 5.1.0, it is possible to refer to existing .ini variables
   from within .ini files. Example: open_basedir = ${open_basedir}
   ":/new/dir".
     __________________________________________________________________

How to change configuration settings

Running PHP as an Apache module

   When using PHP as an Apache module, you can also change the
   configuration settings using directives in Apache configuration files
   (e.g. httpd.conf) and .htaccess files. You will need "AllowOverride
   Options" or "AllowOverride All" privileges to do so.

   With PHP 4 and PHP 5, there are several Apache directives that allow
   you to change the PHP configuration from within the Apache
   configuration files. For a listing of which directives are PHP_INI_ALL,
   PHP_INI_PERDIR, or PHP_INI_SYSTEM, have a look at the List of php.ini
   directives appendix.

     Note: With PHP 3, there are Apache directives that correspond to
     each configuration setting in the php3.ini name, except the name is
     prefixed by "php3_".

   php_value name value
          Sets the value of the specified directive. Can be used only with
          PHP_INI_ALL and PHP_INI_PERDIR type directives. To clear a
          previously set value use none as the value.

     Note: Don't use php_value to set boolean values. php_flag (see
     below) should be used instead.

   php_flag name on|off
          Used to set a boolean configuration directive. Can be used only
          with PHP_INI_ALL and PHP_INI_PERDIR type directives.

   php_admin_value name value
          Sets the value of the specified directive. This can not be used
          in .htaccess files. Any directive type set with php_admin_value
          can not be overridden by .htaccess or virtualhost directives. To
          clear a previously set value use none as the value.

   php_admin_flag name on|off
          Used to set a boolean configuration directive. This can not be
          used in .htaccess files. Any directive type set with
          php_admin_flag can not be overridden by .htaccess or virtualhost
          directives.

   Example 5-2. Apache configuration example
<IfModule mod_php5.c>
  php_value include_path ".:/usr/local/lib/php"
  php_admin_flag safe_mode on
</IfModule>

   Caution

   PHP constants do not exist outside of PHP. For example, in httpd.conf
   you can not use PHP constants such as E_ALL or E_NOTICE to set the
   error_reporting directive as they will have no meaning and will
   evaluate to 0. Use the associated bitmask values instead. These
   constants can be used in php.ini
     __________________________________________________________________

Changing PHP configuration via the Windows registry

   When running PHP on Windows, the configuration values can be modified
   on a per-directory basis using the Windows registry. The configuration
   values are stored in the registry key HKLM\SOFTWARE\PHP\Per Directory
   Values, in the sub-keys corresponding to the path names. For example,
   configuration values for the directory c:\inetpub\wwwroot would be
   stored in the key HKLM\SOFTWARE\PHP\Per Directory
   Values\c\inetpub\wwwroot. The settings for the directory would be
   active for any script running from this directory or any subdirectory
   of it. The values under the key should have the name of the PHP
   configuration directive and the string value. PHP constants in the
   values are not parsed. However, only configuration values changeable in
   PHP_INI_USER can be set this way, PHP_INI_PERDIR values can not.
     __________________________________________________________________

Other interfaces to PHP

   Regardless of how you run PHP, you can change certain values at runtime
   of your scripts through ini_set(). See the documentation on the
   ini_set() page for more information.

   If you are interested in a complete list of configuration settings on
   your system with their current values, you can execute the phpinfo()
   function, and review the resulting page. You can also access the values
   of individual configuration directives at runtime using ini_get() or
   get_cfg_var().
     __________________________________________________________________

Chapter 6. Installation FAQ

   This section holds common questions about the way to install PHP. PHP
   is available for almost any OS (except maybe for MacOS before OSX), and
   almost any web server.

   To install PHP, follow the instructions in Installing PHP.

   1. Why shouldn't I use Apache2 with a threaded MPM in a production
          environment?

   2. Unix/Windows: Where should my php.ini file be located?
   3. Unix: I installed PHP, but every time I load a document, I get the
          message 'Document Contains No Data'! What's going on here?

   4. Unix: I installed PHP using RPMS, but Apache isn't processing the
          PHP pages! What's going on here?

   5. Unix: I installed PHP 3 using RPMS, but it doesn't compile with the
          database support I need! What's going on here?

   6. Unix: I patched Apache with the FrontPage extensions patch, and
          suddenly PHP stopped working. Is PHP incompatible with the
          Apache FrontPage extensions?

   7. Unix/Windows: I have installed PHP, but when I try to access a PHP
          script file via my browser, I get a blank screen.

   8. Unix/Windows: I have installed PHP, but when try to access a PHP
          script file via my browser, I get a server 500 error.

   9. Some operating systems: I have installed PHP without errors, but
          when I try to start apache I get undefined symbol errors:

[mybox:user /src/php5] root# apachectl configtest
 apachectl: /usr/local/apache/bin/httpd Undefined symbols:
  _compress
  _uncompress

   10. Windows: I have installed PHP, but when I to access a PHP script
          file via my browser, I get the error:

cgi error:
 The specified CGI application misbehaved by not
 returning a complete set of HTTP headers.
 The headers it did return are:

   11. Windows: I've followed all the instructions, but still can't get
          PHP and IIS to work together!

   12. When running PHP as CGI with IIS, PWS, OmniHTTPD or Xitami, I get
          the following error: Security Alert! PHP CGI cannot be accessed
          directly..

   13. How do I know if my php.ini is being found and read? It seems like
          it isn't as my changes aren't being implemented.

   14. How do I add my PHP directory to the PATH on Windows?
   15. How do I make the php.ini file available to PHP on windows?
   16. Is it possible to use Apache content negotiation (MultiViews
          option) with PHP?

   17. Is PHP limited to process GET and POST request methods only?

   1. Why shouldn't I use Apache2 with a threaded MPM in a production
   environment?

   PHP is glue. It is the glue used to build cool web applications by
   sticking dozens of 3rd-party libraries together and making it all
   appear as one coherent entity through an intuitive and easy to learn
   language interface. The flexibility and power of PHP relies on the
   stability and robustness of the underlying platform. It needs a working
   OS, a working web server and working 3rd-party libraries to glue
   together. When any of these stop working PHP needs ways to identify the
   problems and fix them quickly. When you make the underlying framework
   more complex by not having completely separate execution threads,
   completely separate memory segments and a strong sandbox for each
   request to play in, feet of clay are introduced into PHP's system.

   If you feel you have to use a threaded MPM, look at a FastCGI
   configuration where PHP is running in its own memory space.

   And finally, this warning against using a threaded MPM is not as strong
   for Windows systems because most libraries on that platform tend to be
   threadsafe.

   2. Unix/Windows: Where should my php.ini file be located?

   By default on Unix it should be in /usr/local/lib which is
   <install-path>/lib. Most people will want to change this at
   compile-time with the --with-config-file-path flag. You would, for
   example, set it with something like:
   --with-config-file-path=/etc

   And then you would copy php.ini-production from the distribution to
   /etc/php.ini and edit it to make any local changes you want.
   --with-config-file-scan-dir=PATH

   On Windows the default path for the php.ini file is the Windows
   directory. If you're using the Apache webserver, php.ini is first
   searched in the Apaches install directory, e.g. c:\program files\apache
   group\apache. This way you can have different php.ini files for
   different versions of Apache on the same machine.

   See also the chapter about the configuration file.

   3. Unix: I installed PHP, but every time I load a document, I get the
   message 'Document Contains No Data'! What's going on here?

   This probably means that PHP is having some sort of problem and is
   core-dumping. Look in your server error log to see if this is the case,
   and then try to reproduce the problem with a small test case. If you
   know how to use 'gdb', it is very helpful when you can provide a
   backtrace with your bug report to help the developers pinpoint the
   problem. If you are using PHP as an Apache module try something like:

     * Stop your httpd processes
     * gdb httpd
     * Stop your httpd processes
     * > run -X -f /path/to/httpd.conf
     * Then fetch the URL causing the problem with your browser
     * > run -X -f /path/to/httpd.conf
     * If you are getting a core dump, gdb should inform you of this now
     * type: bt
     * You should include your backtrace in your bug report. This should
       be submitted to http://bugs.php.net/

   If your script uses the regular expression functions (ereg() and
   friends), you should make sure that you compiled PHP and Apache with
   the same regular expression package. This should happen automatically
   with PHP and Apache 1.3.x

   4. Unix: I installed PHP using RPMS, but Apache isn't processing the
   PHP pages! What's going on here?

   Assuming you installed both Apache and PHP from RPM packages, you need
   to uncomment or add some or all of the following lines in your
   httpd.conf file:
# Extra Modules
AddModule mod_php.c
AddModule mod_php3.c
AddModule mod_perl.c

# Extra Modules
LoadModule php_module         modules/mod_php.so
LoadModule perl_module        modules/libperl.so

   And add:
AddType application/x-httpd-php3 .php3    # for PHP 3
AddType application/x-httpd-php .php      # for PHP 4

   ... to the global properties, or to the properties of the VirtualDomain
   you want to have PHP support added to.

   5. Unix: I installed PHP 3 using RPMS, but it doesn't compile with the
   database support I need! What's going on here?

   Due to the way PHP 3 built, it is not easy to build a complete flexible
   PHP RPM. This issue is addressed in PHP 4. For PHP 3, we currently
   suggest you use the mechanism described in the INSTALL.REDHAT file in
   the PHP distribution. If you insist on using an RPM version of PHP 3,
   read on...

   The RPM packagers are setting up the RPMS to install without database
   support to simplify installations and because RPMS use /usr/ instead of
   the standard /usr/local/ directory for files. You need to tell the RPM
   spec file which databases to support and the location of the top-level
   of your database server.

   This example will explain the process of adding support for the popular
   MySQL database server, using the mod installation for Apache.

   Of course all of this information can be adjusted for any database
   server that PHP supports. We will assume you installed MySQL and Apache
   completely with RPMS for this example as well.

     * First remove mod_php3 :

rpm -e mod_php3

     * Then get the source rpm and INSTALL it, NOT --rebuild

rpm -Uvh mod_php3-3.0.5-2.src.rpm

     * Then edit the /usr/src/redhat/SPECS/mod_php3.spec file
       In the %build section add the database support you want, and the
       path.
       For MySQL you would add --with-mysql=/usr The %build section will
       look something like this:

./configure --prefix=/usr \
--with-apxs=/usr/sbin/apxs \
--with-config-file-path=/usr/lib \
--enable-debug=no \
--enable-safe-mode \
--with-exec-dir=/usr/bin \
--with-mysql=/usr \
--with-system-regex

     * Once this modification is made then build the binary rpm as
       follows:

rpm -bb /usr/src/redhat/SPECS/mod_php3.spec

     * Then install the rpm

rpm -ivh /usr/src/redhat/RPMS/i386/mod_php3-3.0.5-2.i386.rpm

   Make sure you restart Apache, and you now have PHP 3 with MySQL support
   using RPM's. Note that it is probably much easier to just build from
   the distribution tarball of PHP 3 and follow the instructions in
   INSTALL.REDHAT found in that distribution.

   6. Unix: I patched Apache with the FrontPage extensions patch, and
   suddenly PHP stopped working. Is PHP incompatible with the Apache
   FrontPage extensions?

   No, PHP works fine with the FrontPage extensions. The problem is that
   the FrontPage patch modifies several Apache structures, that PHP relies
   on. Recompiling PHP (using 'make clean ; make') after the FP patch is
   applied would solve the problem.

   7. Unix/Windows: I have installed PHP, but when I try to access a PHP
   script file via my browser, I get a blank screen.

   Do a 'view source' in the web browser and you will probably find that
   you can see the source code of your PHP script. This means that the web
   server did not send the script to PHP for interpretation. Something is
   wrong with the server configuration - double check the server
   configuration against the PHP installation instructions.

   8. Unix/Windows: I have installed PHP, but when try to access a PHP
   script file via my browser, I get a server 500 error.

   Something went wrong when the server tried to run PHP. To get to see a
   sensible error message, from the command line, change to the directory
   containing the PHP executable (php.exe on Windows) and run php -i. If
   PHP has any problems running, then a suitable error message will be
   displayed which will give you a clue as to what needs to be done next.
   If you get a screen full of HTML codes (the output of the phpinfo()
   function) then PHP is working, and your problem may be related to your
   server configuration which you should double check.

   9. Some operating systems: I have installed PHP without errors, but
   when I try to start apache I get undefined symbol errors:
[mybox:user /src/php5] root# apachectl configtest
 apachectl: /usr/local/apache/bin/httpd Undefined symbols:
  _compress
  _uncompress

   This has actually nothing to do with PHP, but with the MySQL client
   libraries. Some need --with-zlib, others do not. This is also covered
   in the MySQL FAQ.

   10. Windows: I have installed PHP, but when I to access a PHP script
   file via my browser, I get the error:
cgi error:
 The specified CGI application misbehaved by not
 returning a complete set of HTTP headers.
 The headers it did return are:

   This error message means that PHP failed to output anything at all. To
   get to see a sensible error message, from the command line, change to
   the directory containing the PHP executable (php.exe on Windows) and
   run php -i. If PHP has any problems running, then a suitable error
   message will be displayed which will give you a clue as to what needs
   to be done next. If you get a screen full of HTML codes (the output of
   the phpinfo() function) then PHP is working.

   Once PHP is working at the command line, try accessing the script via
   the browser again. If it still fails then it could be one of the
   following:

     * File permissions on your PHP script, php.exe, php5ts.dll, php.ini
       or any PHP extensions you are trying to load are such that the
       anonymous internet user ISUR_<machinename> cannot access them.
     * The script file does not exist (or possibly isn't where you think
       it is relative to your web root directory). Note that for IIS you
       can trap this error by ticking the 'check file exists' box when
       setting up the script mappings in the Internet Services Manager. If
       a script file does not exist then the server will return a 404
       error instead. There is also the additional benefit that IIS will
       do any authentication required for you based on the NTLanMan
       permissions on your script file.

   11. Windows: I've followed all the instructions, but still can't get
   PHP and IIS to work together!

   Make sure any user who needs to run a PHP script has the rights to run
   php.exe! IIS uses an anonymous user which is added at the time IIS is
   installed. This user needs rights to php.exe. Also, any authenticated
   user will also need rights to execute php.exe. And for IIS4 you need to
   tell it that PHP is a script engine. Also, you will want to read this
   faq.

   12. When running PHP as CGI with IIS, PWS, OmniHTTPD or Xitami, I get
   the following error: Security Alert! PHP CGI cannot be accessed
   directly..

   You must set the cgi.force_redirect directive to 0. It defaults to 1 so
   be sure the directive isn't commented out (with a ;). Like all
   directives, this is set in php.ini

   Because the default is 1, it's critical that you're 100% sure that the
   correct php.ini file is being read. Read this faq for details.

   13. How do I know if my php.ini is being found and read? It seems like
   it isn't as my changes aren't being implemented.

   To be sure your php.ini is being read by PHP, make a call to phpinfo()
   and near the top will be a listing called Configuration File (php.ini).
   This will tell you where PHP is looking for php.ini and whether or not
   it's being read. If just a directory PATH exists than it's not being
   read and you should put your php.ini in that directory. If php.ini is
   included within the PATH than it is being read.

   If php.ini is being read and you're running PHP as a module, then be
   sure to restart your web server after making changes to php.ini

   14. How do I add my PHP directory to the PATH on Windows?

   On Windows NT, 2000, XP and 2003:

     * Go to Control Panel and open the System icon (Start -> Settings ->
       Control Panel -> System, or just Start -> Control Panel -> System
       for Windows XP/2003)
     * Go to the Advanced tab
     * Click on the 'Environment Variables' button
     * Look into the 'System Variables' pane
     * Find the Path entry (you may need to scroll to find it)
     * Double click on the Path entry
     * Enter your PHP directory at the end, including ';' before (e.g.
       ;C:\php)
     * Press OK and restart your computer

   On Windows 98/Me you need to edit the autoexec.bat file:

     * Open the Notepad (Start -> Run and enter notepad)
     * Open the C:\autoexec.bat file
     * Locate the line with PATH=C:\WINDOWS;C:\WINDOWS\COMMAND;..... and
       add: ;C:\php to the end of the line
     * Save the file and restart your computer

     Note: Be sure to reboot after following the steps above to ensure
     that the PATH changes are applied.

   The PHP manual used to promote the copying of files into the Windows
   system directory, this is because this directory (C:\Windows, C:\WINNT,
   etc.) is by default in the systems PATH. Copying files into the Windows
   system directory has long since been deprecated and may cause problems.

   15. How do I make the php.ini file available to PHP on windows?

   There are several ways of doing this. If you are using Apache, read
   their installation specific instructions (Apache 1, Apache 2),
   otherwise you must set the PHPRC environment variable:

   On Windows NT, 2000, XP and 2003:

     * Go to Control Panel and open the System icon (Start -> Settings ->
       Control Panel -> System, or just Start -> Control Panel -> System
       for Windows XP/2003)
     * Go to the Advanced tab
     * Click on the 'Environment Variables' button
     * Look into the 'System variables' pane
     * Click on 'New' and enter 'PHPRC' as the variable name and the
       directory where php.ini is located as the variable value (e.g.
       C:\php)
     * Press OK and restart your computer

   On Windows 98/Me you need to edit the autoexec.bat file:

     * Open the Notepad (Start -> Run and enter notepad)
     * Open the C:\autoexec.bat file
     * Add a new line to the end of the file: set PHPRC=C:\php (replace
       C:\php with the directory where php.ini is located). Please note
       that the path cannot contain spaces. For instance, if you have
       installed PHP in C:\Program Files\PHP, you would enter
       C:\PROGRA~1\PHP instead.
     * Save the file and restart your computer

   16. Is it possible to use Apache content negotiation (MultiViews
   option) with PHP?

   If links to PHP files include extension, everything works perfect. This
   FAQ is only for the case when links to PHP files don't include
   extension and you want to use content negotiation to choose PHP files
   from URL with no extension. In this case, replace the line AddType
   application/x-httpd-php .php with:
# PHP 4
AddHandler php-script php
AddType text/html php

# PHP 5
AddHandler php5-script php
AddType text/html php

   This solution doesn't work for Apache 1 as PHP module doesn't catch
   php-script.

   17. Is PHP limited to process GET and POST request methods only?

   No, it is possible to handle any request method, e.g. CONNECT. Proper
   response status can be sent with header(). If only GET and POST methods
   should be handled, it can be achieved with this Apache configuration:
<LimitExcept GET POST>
Deny from all
</LimitExcept>

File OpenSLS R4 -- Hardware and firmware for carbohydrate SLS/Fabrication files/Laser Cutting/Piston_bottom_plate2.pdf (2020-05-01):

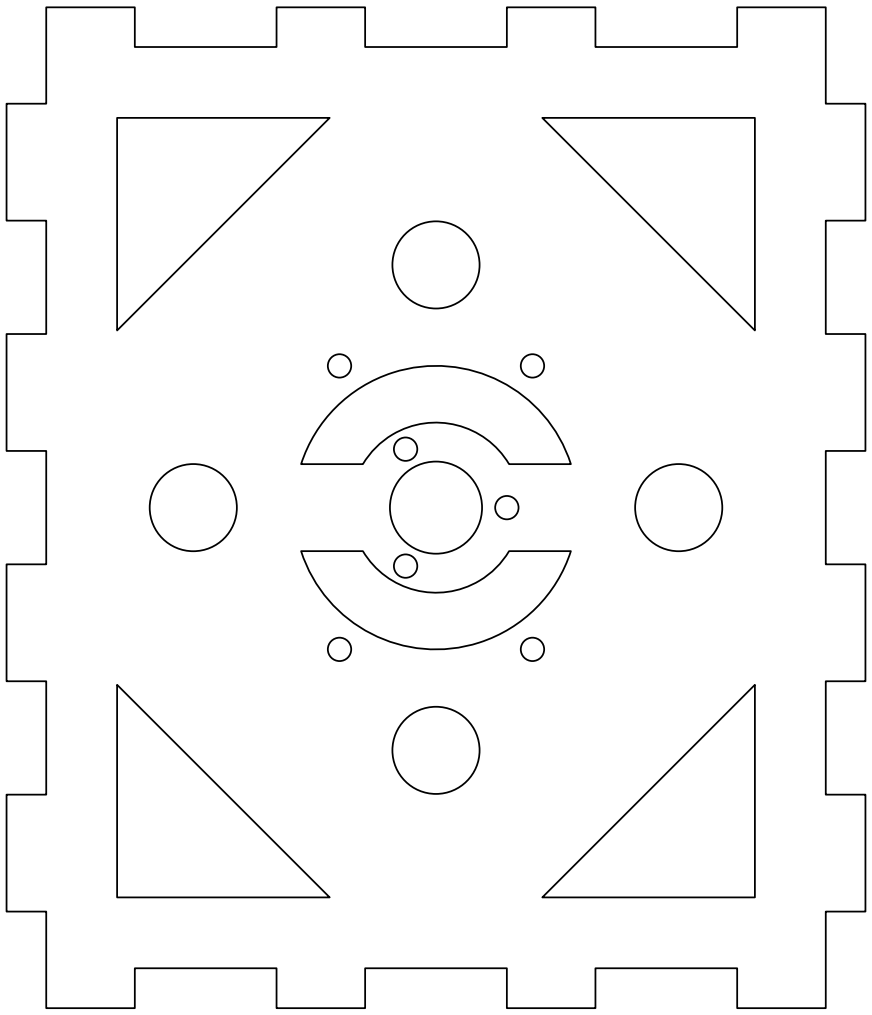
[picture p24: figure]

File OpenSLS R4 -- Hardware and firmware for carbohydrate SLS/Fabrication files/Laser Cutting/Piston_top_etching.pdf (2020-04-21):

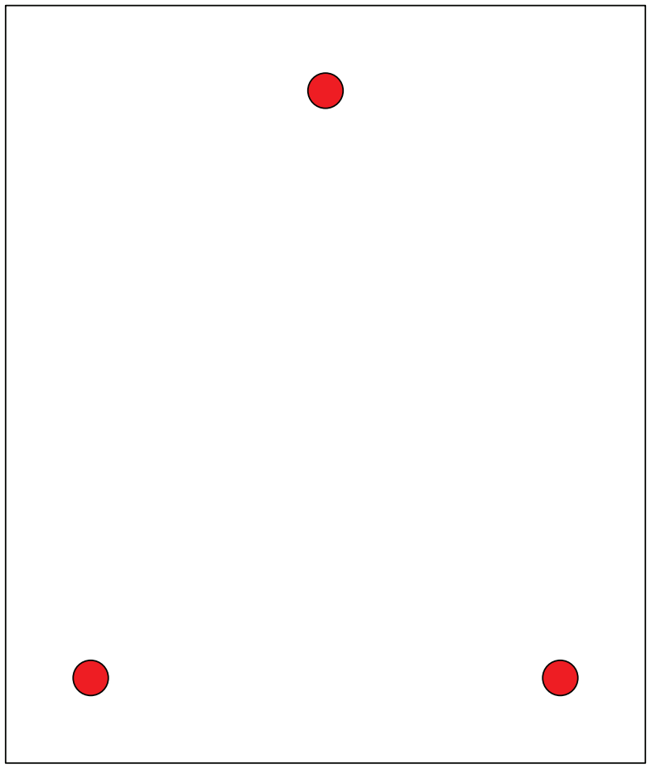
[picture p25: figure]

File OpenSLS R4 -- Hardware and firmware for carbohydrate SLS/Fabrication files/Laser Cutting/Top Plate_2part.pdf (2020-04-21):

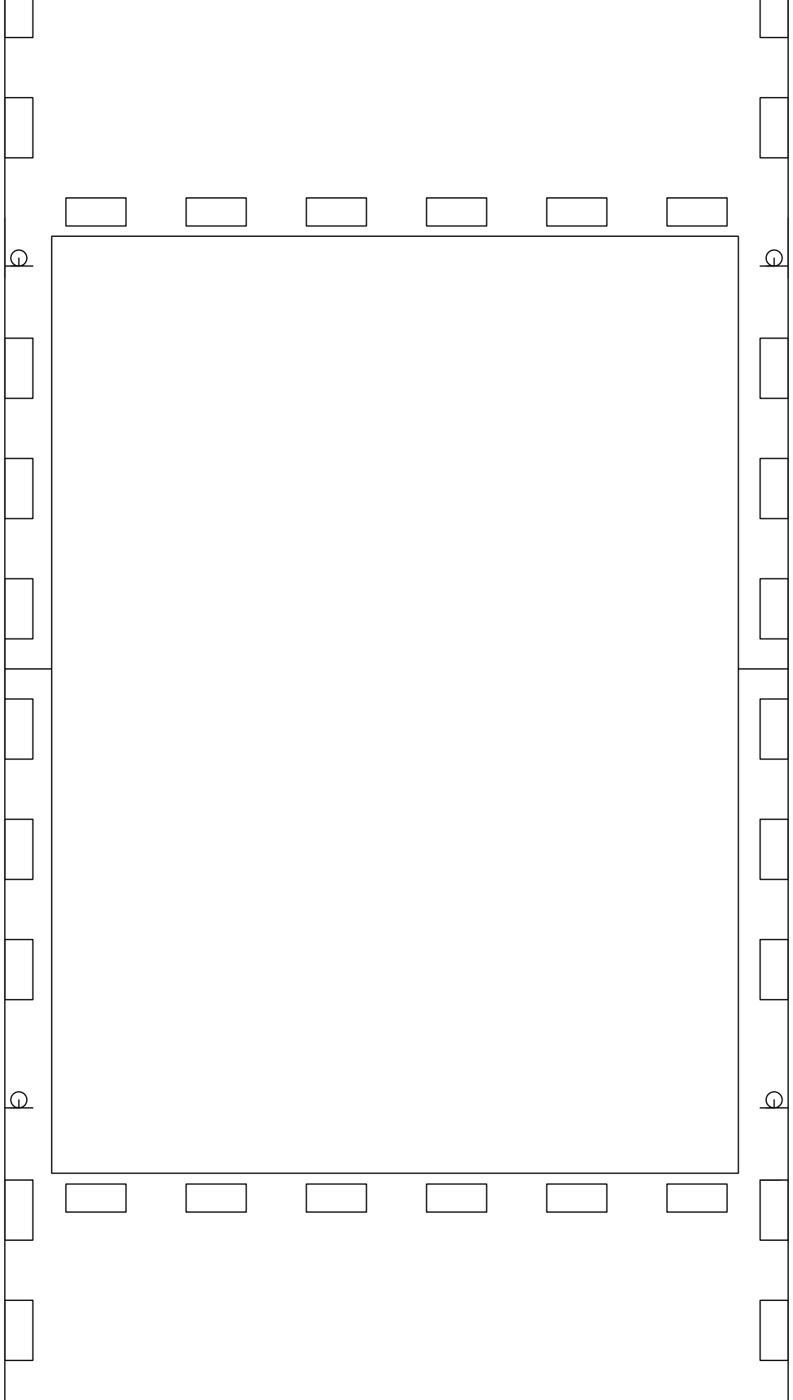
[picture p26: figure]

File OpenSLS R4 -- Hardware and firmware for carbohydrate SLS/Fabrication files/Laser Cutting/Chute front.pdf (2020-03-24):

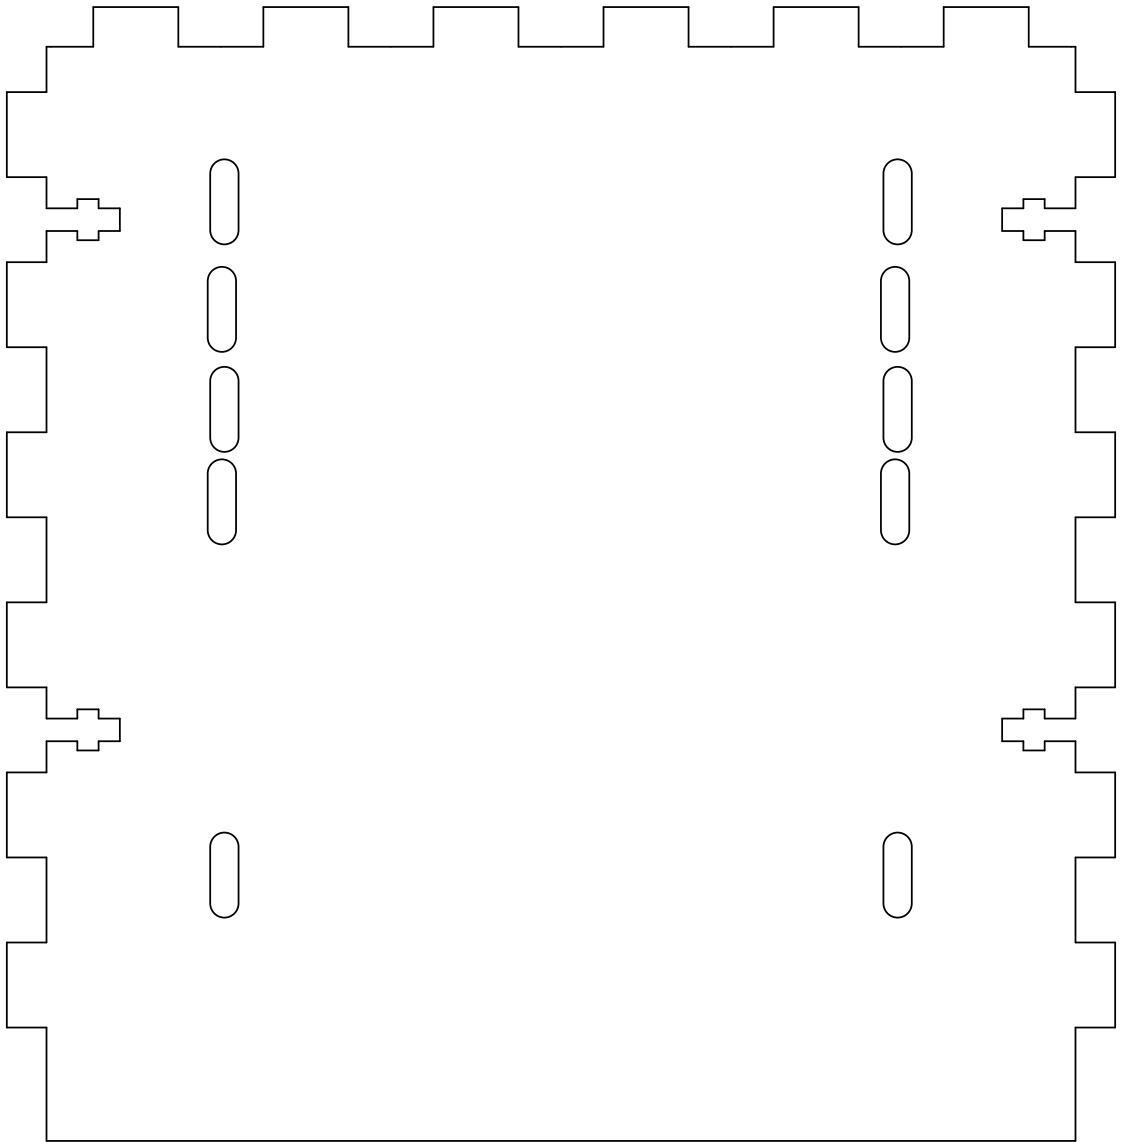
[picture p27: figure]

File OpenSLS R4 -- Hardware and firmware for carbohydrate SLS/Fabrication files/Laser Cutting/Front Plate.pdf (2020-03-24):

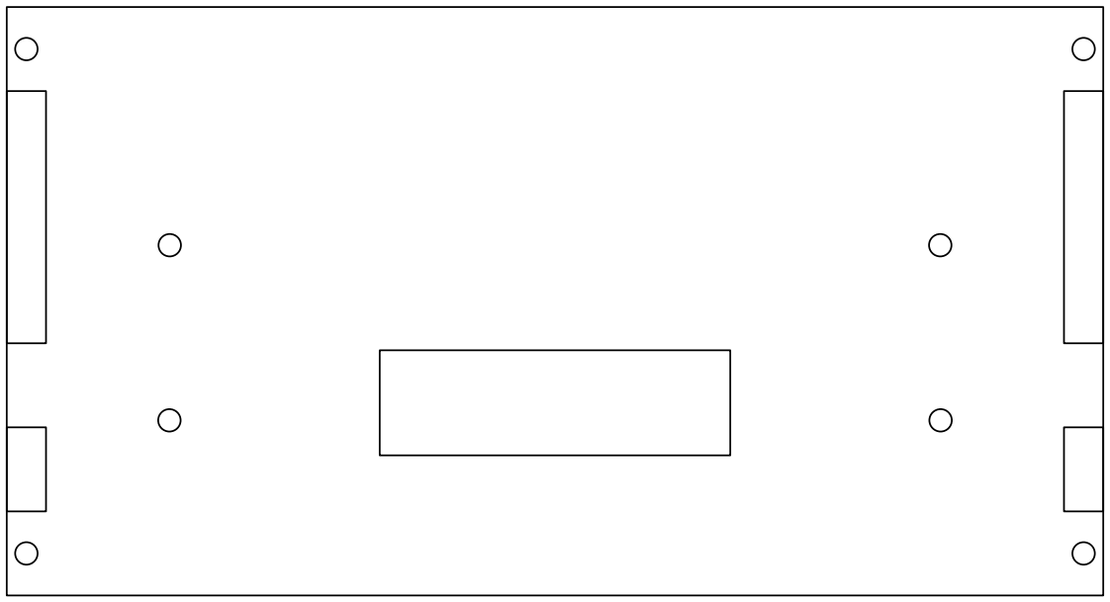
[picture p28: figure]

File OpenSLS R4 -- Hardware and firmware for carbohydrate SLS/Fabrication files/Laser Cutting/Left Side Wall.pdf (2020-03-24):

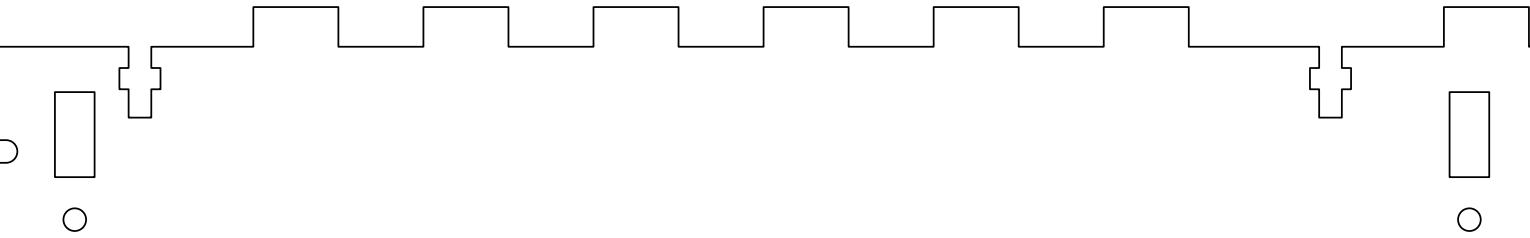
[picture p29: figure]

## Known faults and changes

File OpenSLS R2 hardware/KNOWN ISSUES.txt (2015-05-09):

This is a list of known issues with the R2 hardware:
-The feeder piston printed mounting plate elcipses two tapped M4 holes used to clamp the gasket material.  Functionality is not compromised, but this will be fixed in later revs.\
-Electronics mounting holes for the RAMBO and Arduino need to be relocated.
-No fabrication information for Aluminum print piston
-

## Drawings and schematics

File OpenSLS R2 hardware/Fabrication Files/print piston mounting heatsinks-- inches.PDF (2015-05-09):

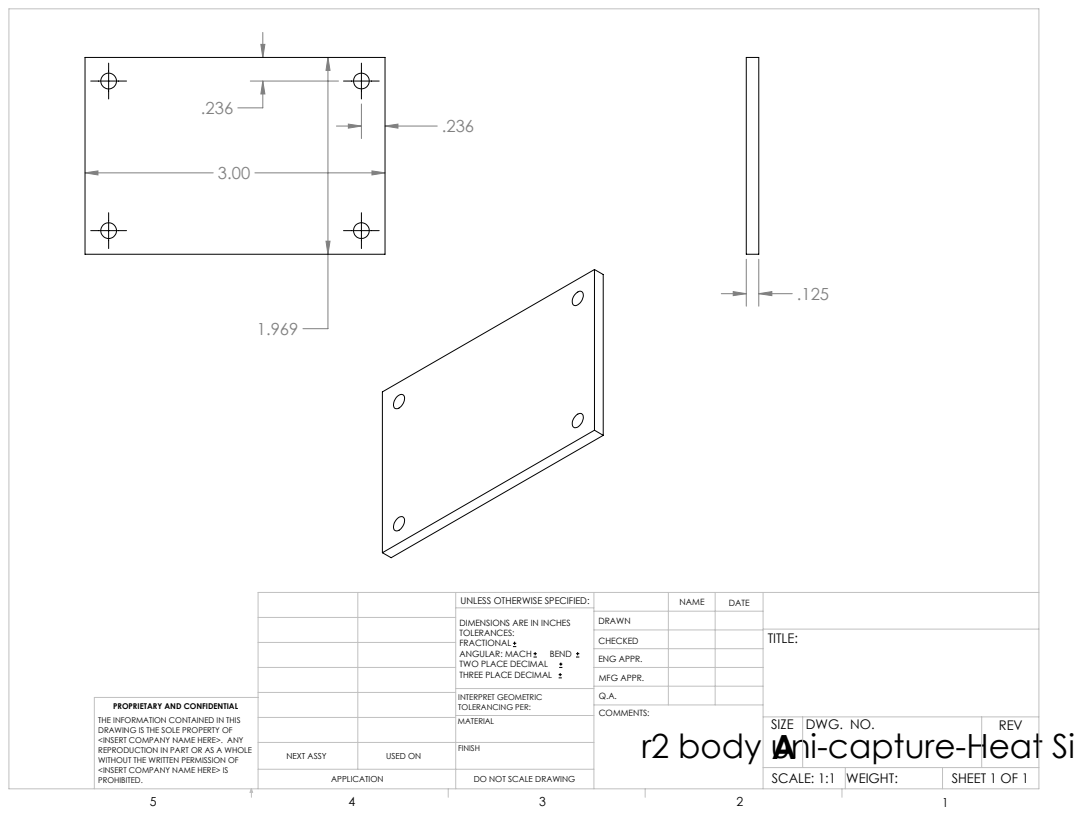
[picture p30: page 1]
SHEET 1 OF 1; SCALE: 1:1 WEIGHT:; DWG. NO.; REV; INTERPRET GEOMETRIC TOLERANCING PER:; ANGULAR: MACH; BEND; NEXT ASSY; USED ON

UNLESS OTHERWISE SPECIFIED:

DIMENSIONS ARE IN INCHES
TOLERANCES:
FRACTIONAL
TWO PLACE DECIMAL
THREE PLACE DECIMAL

DRAWN
CHECKED
ENG APPR.
MFG APPR.
COMMENTS:
r2 body uni-capture-Heat Sink A

PROPRIETARY AND CONFIDENTIAL
THE INFORMATION CONTAINED IN THIS
DRAWING IS THE SOLE PROPERTY OF
<INSERT COMPANY NAME HERE>. ANY
REPRODUCTION IN PART OR AS A WHOLE
WITHOUT THE WRITTEN PERMISSION OF
<INSERT COMPANY NAME HERE> IS
PROHIBITED.

DO NOT SCALE DRAWING

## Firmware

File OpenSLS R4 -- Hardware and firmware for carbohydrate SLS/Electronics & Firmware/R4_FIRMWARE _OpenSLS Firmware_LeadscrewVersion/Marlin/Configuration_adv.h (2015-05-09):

#ifndef CONFIGURATION_ADV_H
#define CONFIGURATION_ADV_H

//===========================================================================
//=============================Thermal Settings  ============================
//===========================================================================

#ifdef BED_LIMIT_SWITCHING
  #define BED_HYSTERESIS 2 //only disable heating if T>target+BED_HYSTERESIS and enable heating if T>target-BED_HYSTERESIS
#endif
#define BED_CHECK_INTERVAL 5000 //ms between checks in bang-bang control

//// Heating sanity check:
// This waits for the watchperiod in milliseconds whenever an M104 or M109 increases the target temperature
// If the temperature has not increased at the end of that period, the target temperature is set to zero. 
// It can be reset with another M104/M109. This check is also only triggered if the target temperature and the current temperature
//  differ by at least 2x WATCH_TEMP_INCREASE
//#define WATCH_TEMP_PERIOD 40000 //40 seconds
//#define WATCH_TEMP_INCREASE 10  //Heat up at least 10 degree in 20 seconds

#ifdef PIDTEMP
  // this adds an experimental additional term to the heatingpower, proportional to the extrusion speed.
  // if Kc is choosen well, the additional required power due to increased melting should be compensated.
  #define PID_ADD_EXTRUSION_RATE  
  #ifdef PID_ADD_EXTRUSION_RATE
    #define  DEFAULT_Kc (1) //heatingpower=Kc*(e_speed)
  #endif
#endif


//automatic temperature: The hot end target temperature is calculated by all the buffered lines of gcode.
//The maximum buffered steps/sec of the extruder motor are called "se".
//You enter the autotemp mode by a M109 S<mintemp> T<maxtemp> F<factor>
// the target temperature is set to mintemp+factor*se[steps/sec] and limited by mintemp and maxtemp
// you exit the value by any M109 without F*
// Also, if the temperature is set to a value <mintemp, it is not changed by autotemp.
// on an ultimaker, some initial testing worked with M109 S215 B260 F1 in the start.gcode
#define AUTOTEMP
#ifdef AUTOTEMP
  #define AUTOTEMP_OLDWEIGHT 0.98
#endif

//  extruder run-out prevention. 
//if the machine is idle, and the temperature over MINTEMP, every couple of SECONDS some filament is extruded
//#define EXTRUDER_RUNOUT_PREVENT  
#define EXTRUDER_RUNOUT_MINTEMP 190  
#define EXTRUDER_RUNOUT_SECONDS 30.
#define EXTRUDER_RUNOUT_ESTEPS 14. //mm filament
#define EXTRUDER_RUNOUT_SPEED 1500.  //extrusion speed
#define EXTRUDER_RUNOUT_EXTRUDE 100

//These defines help to calibrate the AD595 sensor in case you get wrong temperature measurements.
//The measured temperature is defined as "actualTemp = (measuredTemp * TEMP_SENSOR_AD595_GAIN) + TEMP_SENSOR_AD595_OFFSET"
#define TEMP_SENSOR_AD595_OFFSET 0.0
#define TEMP_SENSOR_AD595_GAIN   1.0

//This is for controlling a fan to cool down the stepper drivers
//it will turn on when any driver is enabled
//and turn off after the set amount of seconds from last driver being disabled again
#define CONTROLLERFAN_PIN -1 //Pin used for the fan to cool controller (-1 to disable)
#define CONTROLLERFAN_SECS 60 //How many seconds, after all motors were disabled, the fan should run
#define CONTROLLERFAN_SPEED 255  // == full speed

// When first starting the main fan, run it at full speed for the
// given number of milliseconds.  This gets the fan spinning reliably
// before setting a PWM value. (Does not work with software PWM for fan on Sanguinololu)
//#define FAN_KICKSTART_TIME 100

// Extruder cooling fans
// Configure fan pin outputs to automatically turn on/off when the associated
// extruder temperature is above/below EXTRUDER_AUTO_FAN_TEMPERATURE.
// Multiple extruders can be assigned to the same pin in which case 
// the fan will turn on when any selected extruder is above the threshold.
#define EXTRUDER_0_AUTO_FAN_PIN   -1
#define EXTRUDER_1_AUTO_FAN_PIN   -1
#define EXTRUDER_2_AUTO_FAN_PIN   -1
#define EXTRUDER_AUTO_FAN_TEMPERATURE 50
#define EXTRUDER_AUTO_FAN_SPEED   255  // == full speed


//===========================================================================
//=============================Mechanical Settings===========================
//===========================================================================

#define ENDSTOPS_ONLY_FOR_HOMING // If defined the endstops will only be used for homing


//// AUTOSET LOCATIONS OF LIMIT SWITCHES
//// Added by ZetaPhoenix 09-15-2012
#ifdef MANUAL_HOME_POSITIONS  // Use manual limit switch locations
  #define X_HOME_POS MANUAL_X_HOME_POS
  #define Y_HOME_POS MANUAL_Y_HOME_POS
  #define Z_HOME_POS MANUAL_Z_HOME_POS
#else //Set min/max homing switch positions based upon homing direction and min/max travel limits
  //X axis
  #if X_HOME_DIR == -1
    #ifdef BED_CENTER_AT_0_0
      #define X_HOME_POS X_MAX_LENGTH * -0.5
    #else
      #define X_HOME_POS X_MIN_POS
    #endif //BED_CENTER_AT_0_0
  #else    
    #ifdef BED_CENTER_AT_0_0
      #define X_HOME_POS X_MAX_LENGTH * 0.5
    #else
      #define X_HOME_POS X_MAX_POS
    #endif //BED_CENTER_AT_0_0
  #endif //X_HOME_DIR == -1
  
  //Y axis
  #if Y_HOME_DIR == -1
    #ifdef BED_CENTER_AT_0_0
      #define Y_HOME_POS Y_MAX_LENGTH * -0.5
    #else
      #define Y_HOME_POS Y_MIN_POS
    #endif //BED_CENTER_AT_0_0
  #else    
    #ifdef BED_CENTER_AT_0_0
      #define Y_HOME_POS Y_MAX_LENGTH * 0.5
    #else
      #define Y_HOME_POS Y_MAX_POS
    #endif //BED_CENTER_AT_0_0
  #endif //Y_HOME_DIR == -1
  
  // Z axis
  #if Z_HOME_DIR == -1 //BED_CENTER_AT_0_0 not used
    #define Z_HOME_POS Z_MIN_POS
  #else    
    #define Z_HOME_POS Z_MAX_POS
  #endif //Z_HOME_DIR == -1
#endif //End auto min/max positions
//END AUTOSET LOCATIONS OF LIMIT SWITCHES -ZP


//#define Z_LATE_ENABLE // Enable Z the last moment. Needed if your Z driver overheats.

// A single Z stepper driver is usually used to drive 2 stepper motors.
// Uncomment this define to utilize a separate stepper driver for each Z axis motor.
// Only a few motherboards support this, like RAMPS, which have dual extruder support (the 2nd, often unused, extruder driver is used
// to control the 2nd Z axis stepper motor). The pins are currently only defined for a RAMPS motherboards.
// On a RAMPS (or other 5 driver) motherboard, using this feature will limit you to using 1 extruder.
//#define Z_DUAL_STEPPER_DRIVERS

#ifdef Z_DUAL_STEPPER_DRIVERS
  #undef EXTRUDERS
  #define EXTRUDERS 1
#endif

// Enable this for dual x-carriage printers. 
// A dual x-carriage design has the advantage that the inactive extruder can be parked which
// prevents hot-end ooze contaminating the print. It also reduces the weight of each x-carriage
// allowing faster printing speeds.
//#define DUAL_X_CARRIAGE
#ifdef DUAL_X_CARRIAGE
// Configuration for second X-carriage
// Note: the first x-carriage is defined as the x-carriage which homes to the minimum endstop;
// the second x-carriage always homes to the maximum endstop.
#define X2_MIN_POS 80     // set minimum to ensure second x-carriage doesn't hit the parked first X-carriage
#define X2_MAX_POS 353    // set maximum to the distance between toolheads when both heads are homed 
#define X2_HOME_DIR 1     // the second X-carriage always homes to the maximum endstop position
#define X2_HOME_POS X2_MAX_POS // default home position is the maximum carriage position 
    // However: In this mode the EXTRUDER_OFFSET_X value for the second extruder provides a software 
    // override for X2_HOME_POS. This also allow recalibration of the distance between the two endstops
    // without modifying the firmware (through the "M218 T1 X???" command).
    // Remember: you should set the second extruder x-offset to 0 in your slicer.

// Pins for second x-carriage stepper driver (defined here to avoid further complicating pins.h)
#define X2_ENABLE_PIN 29
#define X2_STEP_PIN 25
#define X2_DIR_PIN 23

// There are a few selectable movement modes for dual x-carriages using M605 S<mode>
//    Mode 0: Full control. The slicer has full control over both x-carriages and can achieve optimal travel results
//                           as long as it supports dual x-carriages. (M605 S0)
//    Mode 1: Auto-park mode. The firmware will automatically park and unpark the x-carriages on tool changes so
//                           that additional slicer support is not required. (M605 S1)
//    Mode 2: Duplication mode. The firmware will transparently make the second x-carriage and extruder copy all  
//                           actions of the first x-carriage. This allows the printer to print 2 arbitrary items at
//                           once. (2nd extruder x offset and temp offset are set using: M605 S2 [Xnnn] [Rmmm])

// This is the default power-up mode which can be later using M605. 
#define DEFAULT_DUAL_X_CARRIAGE_MODE 0 

// As the x-carriages are independent we can now account for any relative Z offset
#define EXTRUDER1_Z_OFFSET 0.0           // z offset relative to extruder 0

// Default settings in "Auto-park Mode" 
#define TOOLCHANGE_PARK_ZLIFT   0.2      // the distance to raise Z axis when parking an extruder
#define TOOLCHANGE_UNPARK_ZLIFT 1        // the distance to raise Z axis when unparking an extruder

// Default x offset in duplication mode (typically set to half print bed width)
#define DEFAULT_DUPLICATION_X_OFFSET 100

#endif //DUAL_X_CARRIAGE
    
//homing hits the endstop, then retracts by this distance, before it tries to slowly bump again:
#define X_HOME_RETRACT_MM 5 
#define Y_HOME_RETRACT_MM 5 
#define Z_HOME_RETRACT_MM 1 
#define QUICK_HOME  //if this is defined, if both x and y are to be homed, a diagonal move will be performed initially.

#define AXIS_RELATIVE_MODES {false, false, false, false}

#define MAX_STEP_FREQUENCY 40000 // Max step frequency for Ultimaker (5000 pps / half step)

//By default pololu step drivers require an active high signal. However, some high power drivers require an active low signal as step.
#define INVERT_X_STEP_PIN false
#define INVERT_Y_STEP_PIN false
#define INVERT_Z_STEP_PIN false
#define INVERT_E_STEP_PIN false

//default stepper release if idle
// AMRI Laser cutter
#define DEFAULT_STEPPER_DEACTIVE_TIME 0

// LMN Laser cutter
//#define DEFAULT_STEPPER_DEACTIVE_TIME 60

#define DEFAULT_MINIMUMFEEDRATE       0.0     // minimum feedrate
#define DEFAULT_MINTRAVELFEEDRATE     0.0

// Feedrates for manual moves along X, Y, Z, E from panel
#ifdef ULTIPANEL
#define MANUAL_FEEDRATE {50*60, 50*60, 4*60, 60}  // set the speeds for manual moves (mm/min)
#endif

// minimum time in microseconds that a movement needs to take if the buffer is emptied.
#define DEFAULT_MINSEGMENTTIME        20000

// If defined the movements slow down when the look ahead buffer is only half full
#define SLOWDOWN

// Frequency limit
// See nophead's blog for more info
// Not working O
//#define XY_FREQUENCY_LIMIT  15

// Minimum planner junction speed. Sets the default minimum speed the planner plans for at the end
// of the buffer and all stops. This should not be much greater than zero and should only be changed
// if unwanted behavior is observed on a user's machine when running at very slow speeds.
#define MINIMUM_PLANNER_SPEED 0.05// (mm/sec)

// MS1 MS2 Stepper Driver Microstepping mode table
#define MICROSTEP1 LOW,LOW
#define MICROSTEP2 HIGH,LOW
#define MICROSTEP4 LOW,HIGH
#define MICROSTEP8 HIGH,HIGH
#define MICROSTEP16 HIGH,HIGH

// Microstep setting (Only functional when stepper driver microstep pins are connected to MCU.
#define MICROSTEP_MODES {16,16,16,16,16} // [1,2,4,8,16]

// Motor Current setting (Only functional when motor driver current ref pins are connected to a digital trimpot on supported boards)
#define DIGIPOT_MOTOR_CURRENT {135,135,135,135,135} // Values 0-255 (RAMBO 135 = ~0.75A, 185 = ~1A)


//===========================================================================
//=============================Additional Features===========================
//===========================================================================
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

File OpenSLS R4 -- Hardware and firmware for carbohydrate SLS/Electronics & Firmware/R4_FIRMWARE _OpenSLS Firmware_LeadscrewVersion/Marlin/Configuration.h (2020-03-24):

#ifndef CONFIGURATION_H
#define CONFIGURATION_H

// This configuration file contains the basic settings.
// Advanced settings can be found in Configuration_adv.h
// BASIC SETTINGS: select your board type, temperature sensor type, axis scaling, and endstop configuration

// User-specified version info of this build to display in [Pronterface, etc] terminal window during
// startup. Implementation of an idea by Prof Braino to inform user that any changes made to this
// build by the user have been successfully uploaded into firmware.
#define STRING_VERSION_CONFIG_H __DATE__ " " __TIME__ // build date and time
#define STRING_CONFIG_H_AUTHOR "(ata, SLS)" // Who made the changes.

// SERIAL_PORT selects which serial port should be used for communication with the host.
// This allows the connection of wireless adapters (for instance) to non-default port pins.
// Serial port 0 is still used by the Arduino bootloader regardless of this setting.
#define SERIAL_PORT 0

// This determines the communication speed of the printer
//#define BAUDRATE 250000
#define BAUDRATE 115200

//// The following define selects which electronics board you have. Please choose the one that matches your setup
// 10 = Gen7 custom (Alfons3 Version) "https://github.com/Alfons3/Generation_7_Electronics"
// 11 = Gen7 v1.1, v1.2 = 11
// 12 = Gen7 v1.3
// 13 = Gen7 v1.4
// 3  = MEGA/RAMPS up to 1.2 = 3
// 33 = RAMPS 1.3 / 1.4 (Power outputs: Extruder, Fan, Bed)
// 34 = RAMPS 1.3 / 1.4 (Power outputs: Extruder0, Extruder1, Bed)
// 35 = RAMPS 1.3 / 1.4 (Power outputs: Extruder, Fan, Fan)
// 4  = Duemilanove w/ ATMega328P pin assignment
// 5  = Gen6
// 51 = Gen6 deluxe
// 6  = Sanguinololu < 1.2
// 62 = Sanguinololu 1.2 and above
// 63 = Melzi
// 64 = STB V1.1
// 65 = Azteeg X1
// 66 = Melzi with ATmega1284 (MaKr3d version)
// 7  = Ultimaker
// 71 = Ultimaker (Older electronics. Pre 1.5.4. This is rare)
// 77 = 3Drag Controller
// 8  = Teensylu
// 80 = Rumba
// 81 = Printrboard (AT90USB1286)
// 82 = Brainwave (AT90USB646)
// 9  = Gen3+
// 70 = Megatronics
// 701= Megatronics v2.0
// 702= Minitronics v1.0
// 90 = Alpha OMCA board
// 91 = Final OMCA board
// 301 = Rambo
// 21 = Elefu Ra Board (v3)

#ifndef MOTHERBOARD
#define MOTHERBOARD 301
#endif

// Define this to set a custom name for your generic Mendel,
// #define CUSTOM_MENDEL_NAME "This Mendel"

// This defines the number of extruders
#define EXTRUDERS 2

//// The following define selects which power supply you have. Please choose the one that matches your setup
// 1 = ATX
// 2 = X-Box 360 203Watts (the blue wire connected to PS_ON and the red wire to VCC)

#define POWER_SUPPLY 1

//===========================================================================
//============================= Laser Settings ==============================
//===========================================================================
//
// Laser control is used by the Muve1 3D printer and the Buildlog.net laser cutter
//
#define LASER
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

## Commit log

2015-05-09 Initial commit 05092015
    [0.5mm and 0.75mm Feed Piston Felt Gaskets.SLDDRW, 2.83mm Acrylic Parts.DXF, 2.83mm Acrylic Parts.SLDDRW, 5.6mm layout 1.DXF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]
2015-05-17 Added BOM
    [Menu Plans.xlsx, OpenSLS Bill of Materials.xlsx]
2016-02-11 Add R3 hardware, Python munge utility
    [BearingCasing with Motor Housing.STL, BearingCasing.STL, BearingHalf2_print2.STL, Bearinghalf1_print2.STL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]
2017-05-09 Update R3 BOM, fix markdown in readme
    [BearingCasing with Motor Housing.STL, BearingCasing.STL, BearingHalf2_print2.STL, Bearinghalf1_print2.STL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]
2020-03-24 Powderbox design files
    [Bushing Sandwich - Bottom.stl, Bushing Sandwich - Top.stl, Chute back.dxf, Chute front.dxf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]
2020-04-21 Update some laser cutting files for R4
    [Piston_bottom_plate.dxf, Piston_top_3mmholes.dxf, Piston_top_etching.dxf, Piston_topmount.dxf]
2020-05-01 Fix piston bottom lasercutting files
    [Piston_bottom_plate.dxf, Piston_bottom_plate2.dxf]
2020-10-07 Update fabrication files for R4 hardware distributor
    [Crossbeam_servoMount.stl, Rotating bearing holder (L).stl, Rotating bearing holder (R).stl, Servo holder.stl]
